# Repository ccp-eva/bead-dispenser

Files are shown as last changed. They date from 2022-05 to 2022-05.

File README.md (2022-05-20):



# CCP Bead Dispenser

**A DIY USB powered bead dispenser**

> Contains an Arduino sketch that accepts user input (i.e., an integer) and then starts a Nema 14 stepper motor. While the motor rotates, the attached infrared beam module counts objects which break the beam. The motor will stop when the object count equals the provided number by the user. This repo includes all 3d stl files and the construction manual.

---

- [CCP Bead Dispenser](#ccp-bead-dispenser)
  - [Demos](#demos)
  - [Overview](#overview)
    - [Power Supply](#power-supply)
    - [What’s happening](#whats-happening)
      - [Software](#software)
      - [Hardware](#hardware)
  - [Hardware Components](#hardware-components)
  - [Construction Manual](#construction-manual)
    - [Soldering Adafruit Shield on the Arduino](#soldering-adafruit-shield-on-the-arduino)
    - [Wiring the Stepper Motor on the Adafruit Shield](#wiring-the-stepper-motor-on-the-adafruit-shield)
      - [Check which coils make a pair](#check-which-coils-make-a-pair)
      - [Connect the Motor to the Shield](#connect-the-motor-to-the-shield)
    - [IR Breakbeam Sensors Connection](#ir-breakbeam-sensors-connection)
      - [Add DuPont Connectors to the wires](#add-dupont-connectors-to-the-wires)
    - [Connect IR Breakbeam Sensors](#connect-ir-breakbeam-sensors)
    - [Threading](#threading)
    - [Disk Treatment](#disk-treatment)
  - [3D Components Overview](#3d-components-overview)

---

## Demos

https://user-images.githubusercontent.com/9831678/168770235-a08dd8c6-3110-4d33-b17b-d08c474d0a74.mp4

https://user-images.githubusercontent.com/9831678/169273257-3fe446e2-8038-4976-b90e-d845b3b6b8b8.mp4

## Overview

This DIY bead dispenser was used as a companion apparatus for [Sarah Pope-Caldwell’s](https://sarahmichellepope.com/) _Nifty Shifty_ Game Battery. Specifically, the dispenser receives a signal (i.e., a positive integer) from the game, which starts a NEMA 14 stepper motor releasing the number of requested beads. The Arduino sketch was developed by [Steven Kalinke](https://www.eva.mpg.de/de/comparative-cultural-psychology/staff/steven-kalinke/).

Initially, [Dylan T Guenther](https://neurology.ufl.edu/profile/guenther-dylan/) provided us with his modifications from [thingiverse](https://www.thingiverse.com/thing:1771176) dispenser, and then [Raik Pieszek](https://www.eva.mpg.de/comparative-cultural-psychology/staff/raik-pieszek/) made significant modifications to meet our requirements. You will find all the `stl` files within the repository’s [`stl` directory](./stl/).

### Power Supply

We are aware the stepper motor and infrared beams are underpowered by the low voltage/current constraints of the USB 2 protocol (i.e., 5V @ 0.5A). However, throughout the entire hardware engineering process, we tested the dispenser to run with standard USB 2.0 power only and have not observed any drawbacks by under-powering it. The dispenser was also running in high humidity conditions (Congo) for approx. 8h per day over five to six weeks conducted by [Elisa Felsche](https://www.eva.mpg.de/comparative-cultural-psychology/staff/elisa-felsche/). Please refer to the [hardware components](#hardware-components) sections for further details.

### What’s happening

As of Summer 2022, we will work on a version 2 with some soft- and hardware improvements, which are listed below:

#### Software

Check the [issue tab](https://github.com/ccp-eva/bead-dispenser/issues) for open issues!

#### Hardware

- [ ] Use Gewindemuffen, -hülse, or Stangenmutter to replace the plastic pillows, Or better use Gewindestifte/Madenschrauben (M5/60mm) (https://www.fenau.eu/gewindeterminal-mit-innengewinde-linksgewinde-fuer-seil-von-o-3-mm-bis-o-8-mm-v2a.html)
- [ ] Make a design that allows flexible adjustment for the disk hole sizes
- [ ] Heat space for stepper motor
- [ ] Motor Thron
- [ ] Universal mount for the flexible funnel sizes

## Hardware Components

<!-- prettier-ignore -->
| Component                                                                   | Description                                                                                                                                                                                                                                                                                                 | Approx. Price |
| --------------------------------------------------------------------------- | :---------------------------------------------------------------------------------------------------------------------------------------------------------------------------------------------------------------------------------------------------------------------------------------------------------- | ------------- |
| Arduino Uno                                                                 | https://www.amazon.com/Arduino-A000066-ARDUINO-UNO-R3/dp/B008GRTSV6                                                                                                                                                                                                                                         |               |
| Adafruit Motor Shield (2.3)                                                 | https://www.amazon.com/Adafruit-Motor-Stepper-Shield-Arduino/dp/B00PUTH3B0                                                                                                                                                                                                                                  |               |
| … alternatively version 2.0 (cheaper)                                       | https://www.roboter-bausatz.de/p/motor-shield-v2.0-fuer-arduino?sPartner=8&gclid=CjwKCAjw1JeJBhB9EiwAV612y0uTo-yNJ4GlXUTTYTJsgV14ZZIoj7A12Il0sJB5pGVDDNJmeDUyexoCM9cQAvD_BwE                                                                                                                                |               |
| Stepper Motor (Nema 14) Option 1                                            | Polou SY35ST28-0504A (200 steps / 1.8°, 0.1Nm holding torque, 10V @ 0.5A, 20Ω Phase resistance) – [Datasheet](https://www.pololu.com/file/0J688/SY35ST28-0504A.pdf) – https://www.robotshop.com/de/de/10-v-05-a-13-oz-in-zweipoliger-schrittmotor.html                                                      |               |
| Stepper Motor (Nema 14) Option 2                                            | Joy-it Nema14-01 (200 steps / 1.8°, 0.1Nm holding torque, 8V @ 0.4A, 20Ω Phase resistance) — [Datasheet](https://joy-it.net/en/products/NEMA14-01) — https://joy-it.net/en/products/NEMA14-01 or https://www.conrad.de/de/p/joy-it-schrittmotor-nema14-01-0-1-nm-0-4-a-wellen-durchmesser-5-mm-2142507.html |               |
| Adafruit IR Beam Break Sensor Pair (3mm, preferably with DuPont Connectors) | https://www.mouser.de/ProductDetail/Adafruit/2167?qs=GURawfaeGuCJ0J7vogtCzg%3D%3D                                                                                                                                                                                                                           |               |
| USB Wire (Type B from the Arduino to whatever you need on your computer)    | Note, we had some difficulties with USB Adapters, a direct connection is preferred, e.g., USB C to Type B: [USB-Kabel USB 2.0 USB-B Stecker](https://www.conrad.de/de/p/manhattan-usb-kabel-usb-2-0-usb-b-stecker-usb-c-stecker-2-00-m-schwarz-2356814.html)                                                |               |
| Pellets                                                                     | We tested a variety of beads/pellets. A rule of thumb: beads should be a non-reflective surface, as the IR signal can be reflected around the pellet. Wood is good material; we used these wood balls: https://www.holz-allerlei.de/holzkugeln-ohne-bohrung/143/holzkugeln-6-mm-oe-ohne-bohrung?c=34        |               |
| Soldering Iron                                                              |                                                                                                                                                                                                                                                                                                             |               |
| Crimp tool and DuPont Connectors                                            | … to easily connect the IR beam break sensors                                                                                                                                                                                                                                                               |               |
| Threading tap to create threads                                             | … for screws and nuts (M4)                                                                                                                                                                                                                                                                                  |               |

## Construction Manual

### Soldering Adafruit Shield on the Arduino

- [Documentation](https://learn.adafruit.com/adafruit-motor-shield-v2-for-arduino/install-headers)
- [Guide](https://learn.adafruit.com/adafruit-motor-shield-v2-for-arduino/install-headers#installing-with-stacking-headers-405903-16)

- Place the Shield stacking headers on the Adafruit shield (terminals are optional for this setup) and solder them its bottom
- You may need to buy stacking headers as the Adafruit shield does not come with them (it did actually for our case)

<p align="middle">
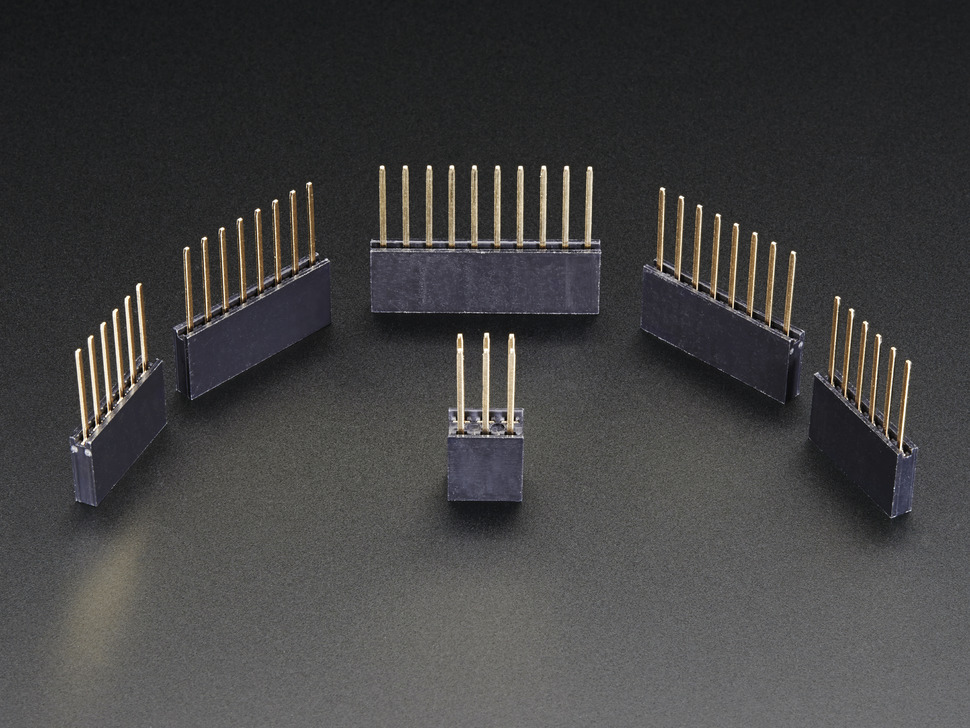
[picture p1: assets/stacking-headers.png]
  
  <br>
  Soldering stacking headers to the Motorshield (they may come pre-soldered for Motor Shield v.2.3)
</p>

### Wiring the Stepper Motor on the Adafruit Shield

#### Check which coils make a pair

Either use a Multimeter and figure out the two wires having the lowest resistance; those make a coil pair. If you do not have a Multimeter, connect their wire tips: Now turn the stepper motor: If the rotation resistance is high, the two cables belong together (i.e., making a coil pair).

#### Connect the Motor to the Shield

<p align="middle">
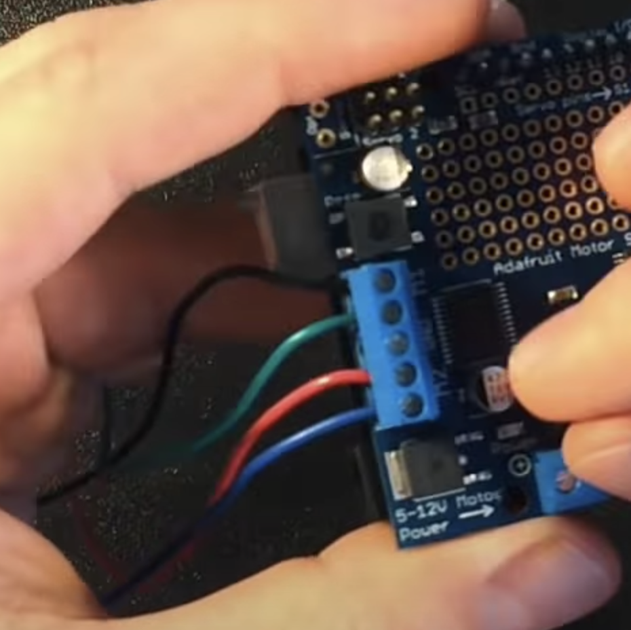
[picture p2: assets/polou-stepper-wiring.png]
  
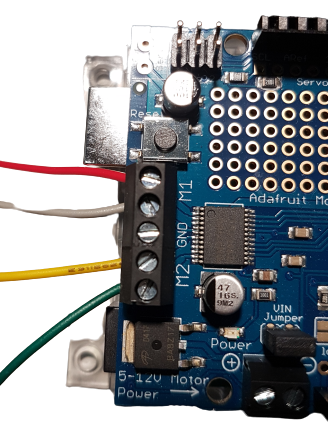
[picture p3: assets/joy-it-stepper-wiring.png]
  <br>
  Left: Polou SY35ST28-0504A (M1: black, green; M2: red, blue). Right: Joy-it Nema14 (M1: red, gray; M2: yellow, green).
</p>

### IR Breakbeam Sensors Connection

Docs & Datasheet: https://www.adafruit.com/product/2167

<p align="middle">
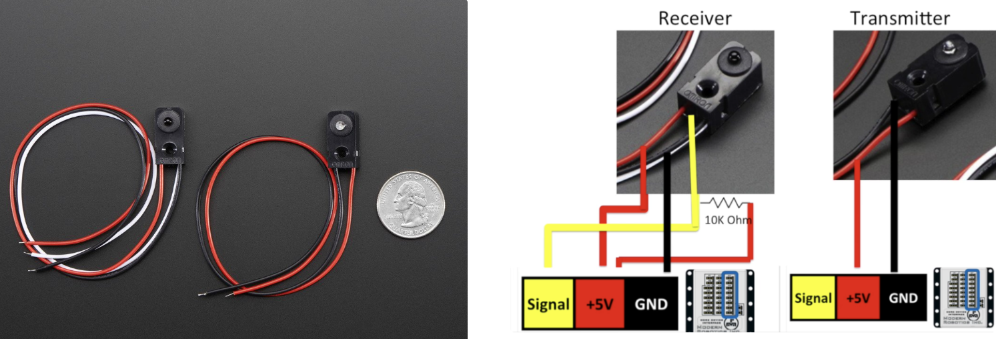
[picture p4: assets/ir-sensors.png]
  
  
  Left Image: The receiver is on the left; it has three wires. The transmitter is on the right; it has two wires.
</p>

#### Add DuPont Connectors to the wires

If your IR break beam sensors came with DuPont (see [JST connector - RE](https://en.wikipedia.org/wiki/JST_connector)) connectors, you can skip this step. If not, use a crimp tool to add crimps.

<p align="middle">
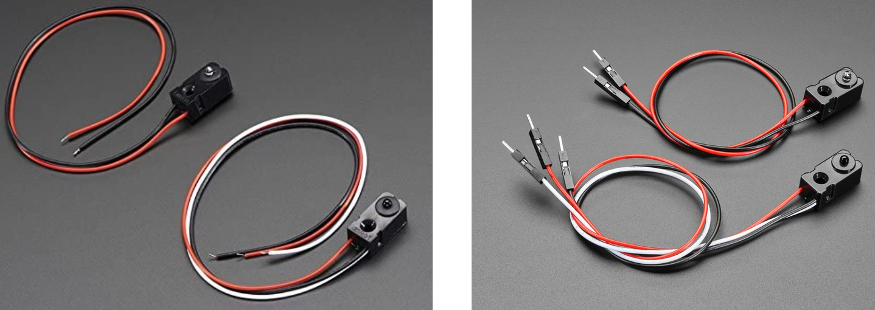
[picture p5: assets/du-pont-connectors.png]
  
  
  Left: IR Breakbeam Sensors w/o DuPont Connectors. Right: IR Breakbeam Sensors w/ DuPont Connectors.
</p>

### Connect IR Breakbeam Sensors

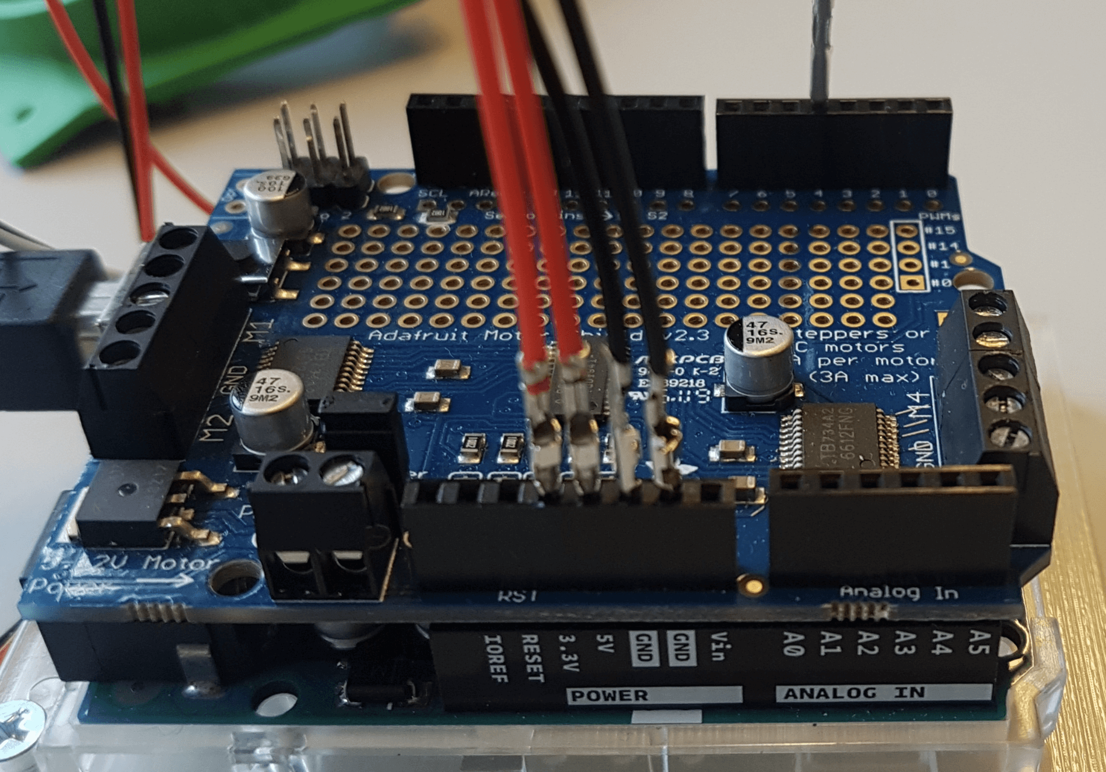
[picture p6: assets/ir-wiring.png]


The **receiver** (photodiode/sensor) has **three** colored wires; connect the

- **black** wire to the ground (there are two, which one doesn’t matter)
- **red** wire to the 5V Pin (**_important!_**)
- **white** wire to Pin 4 in the Digital I/O array

The **transmitter LED** (sender) has **two** colored wires; connect the

- **black** wire to the ground (the one that is left)
- **red** wire to the 3V Pin (**_important!_**)

### Threading

Use **M4 threading taps** for the following 3D components:

<!-- prettier-ignore -->
|  |  |
|-|-|
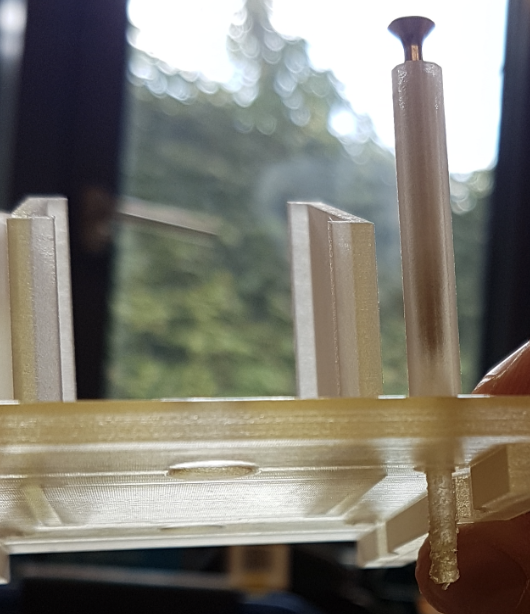
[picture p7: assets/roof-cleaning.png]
| The four pillars from the **roof** print-out (you may need to get rid of some residuals from the print before). Use a screw (or whatever) to push out residuals from the print. Thread after cleaning. |  |
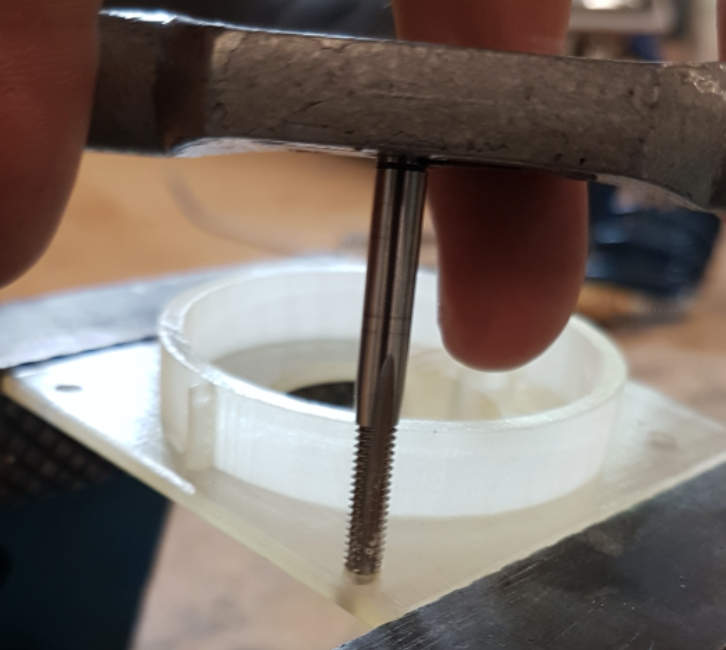
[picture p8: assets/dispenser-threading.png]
| The four holes from the **dispenser** holes |  |
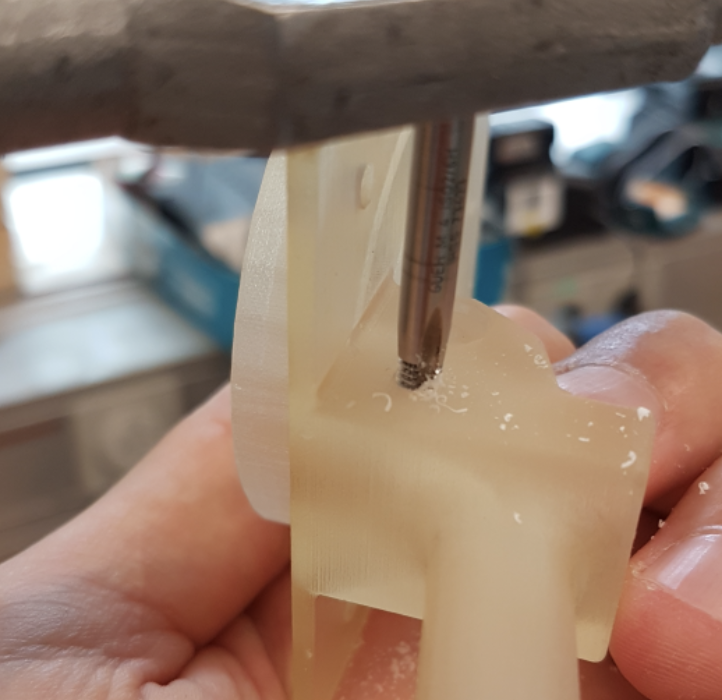
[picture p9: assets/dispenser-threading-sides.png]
| The side of the dispenser. Drill an M4 thread in the side of the dispenser as a fixation for the IR beam breaker |  |
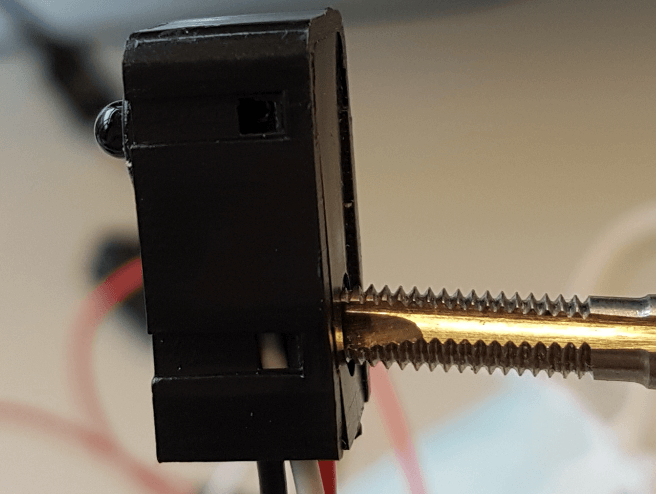
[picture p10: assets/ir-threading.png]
| Finally, drill an M4 thread in the IR break beam transmitter & receiver (this will be screwed together with the dispenser later.  |  |

### Disk Treatment

- Depending on the 3D printer, the bottom of the disk may be a bit rough, therefore creating resistance. Use fine sandpaper to reduce friction.
- Depending on the 3D printer, the disk’s hole may be too narrow for the stepper motor’s D-shaft. Roll a thin layer of sandpaper to increase the inner diameter.

<p align="middle">
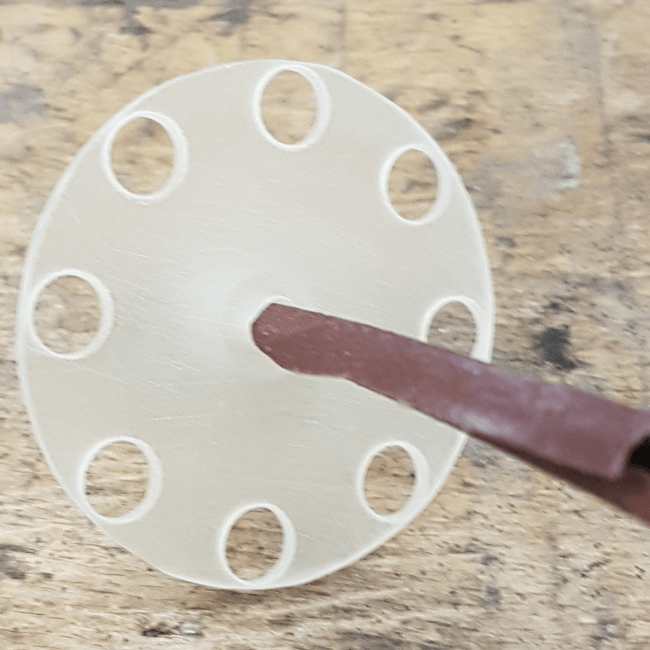
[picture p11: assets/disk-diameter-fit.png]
  
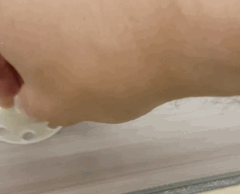
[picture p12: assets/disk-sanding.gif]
  <br>
  Left: Increase inner disk diameter. Right: Sandpaper the bottom of the disk.
</p>

## 3D Components Overview

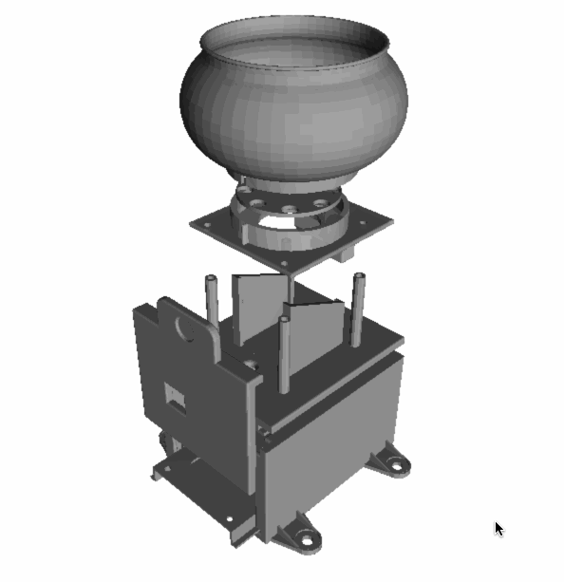
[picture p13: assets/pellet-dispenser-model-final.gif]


Our model is composed of seven components; these are from bottom to top:

- Box
- Slide
- Door
- Roof
- Dispenser
- Disk
- Funnel

<!-- prettier-ignore -->
| Component | STL File | Isometric Preview |
|-|-|-|
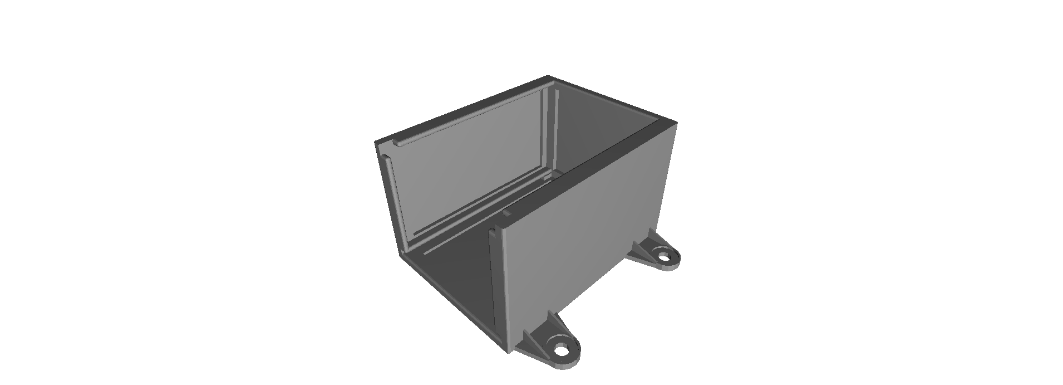
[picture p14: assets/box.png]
| **Box** — Housing for the Arduino & Adafruit Shield | [Download](stl/box.stl) |  |
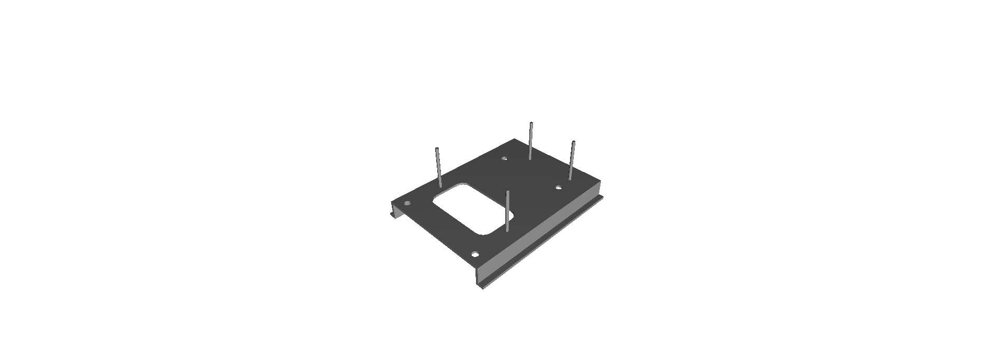
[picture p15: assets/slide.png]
| **Slide** — To fixate the Arduino’s plate with the slide | [Download](stl/slide.stl) |  |
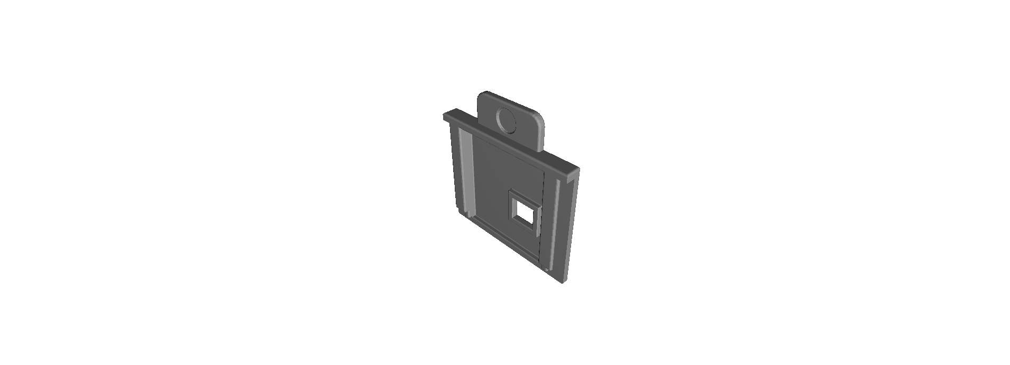
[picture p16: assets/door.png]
| **Door** — Sliding door that closes the box | [Download](stl/door.stl) |  |
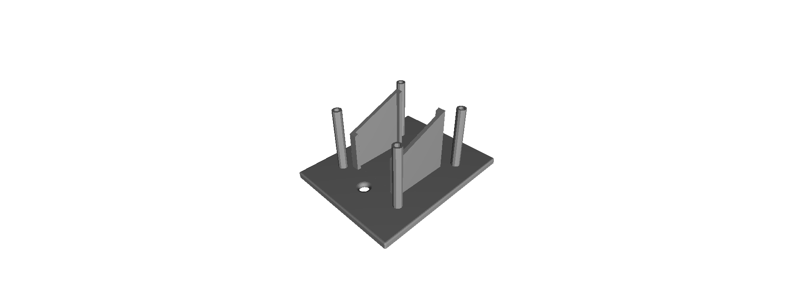
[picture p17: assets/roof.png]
| **Roof** — Coveres the box, and provides a housing for a NEMA 14 stepper motor | [Download](stl/roof.stl) |  |
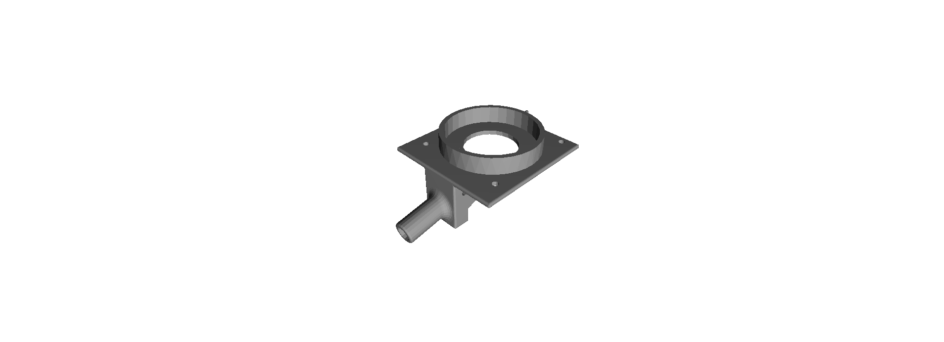
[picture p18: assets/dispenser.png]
| **Dispenser** — Holding the disc and provides a tube | [Download](stl/dispenser.stl) |  |
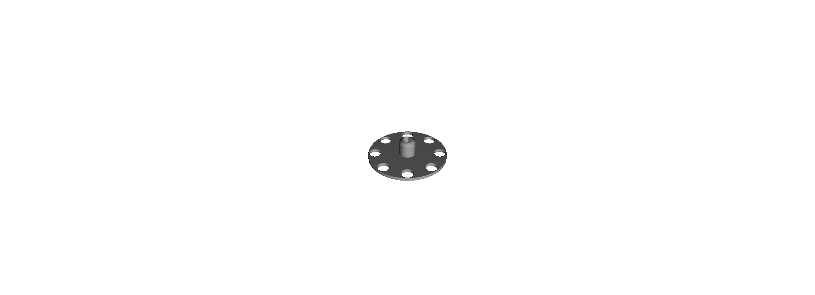
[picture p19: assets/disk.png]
| **Disk** — Revolving magazine to release beads or other objects | [Download](stl/disk.stl) |  |
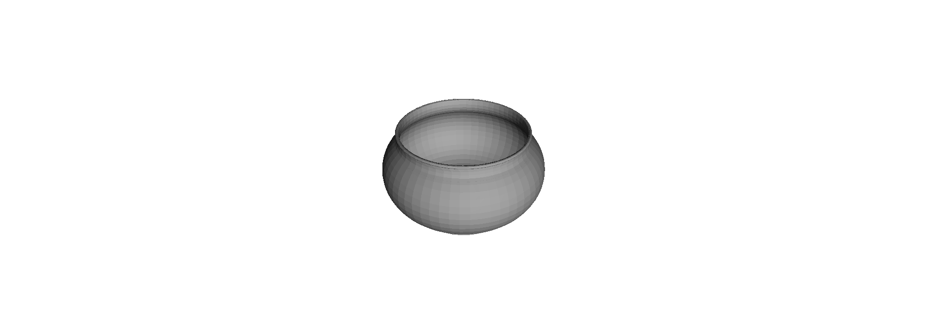
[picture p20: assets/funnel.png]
| **Funnel** — Bead funnel/storage unit | [Download](stl/funnel.stl) |  |
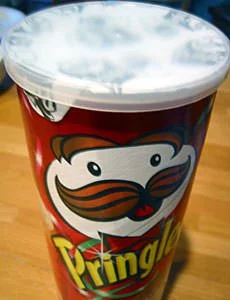
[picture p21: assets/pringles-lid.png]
| **Lid** — Get yourself some Pringles. Use the Pringle’s lid to seal the funnel. (optional) | — |  |

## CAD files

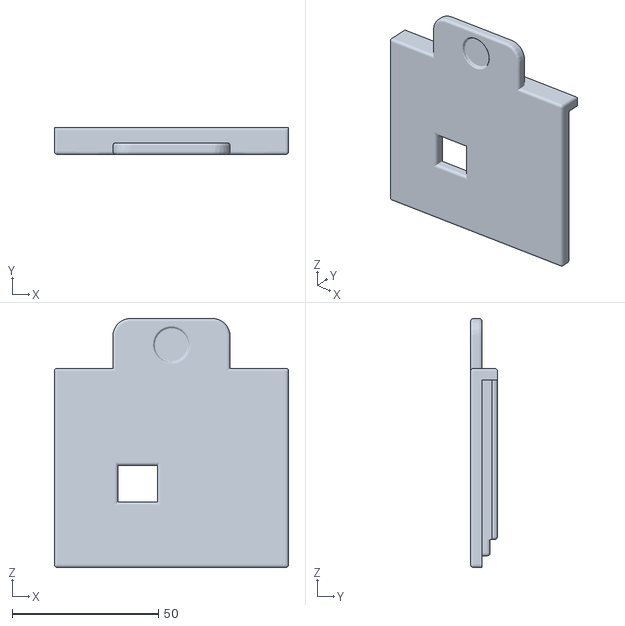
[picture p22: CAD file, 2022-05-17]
stl/door.stl
80.0 x 9.20 x 85.0

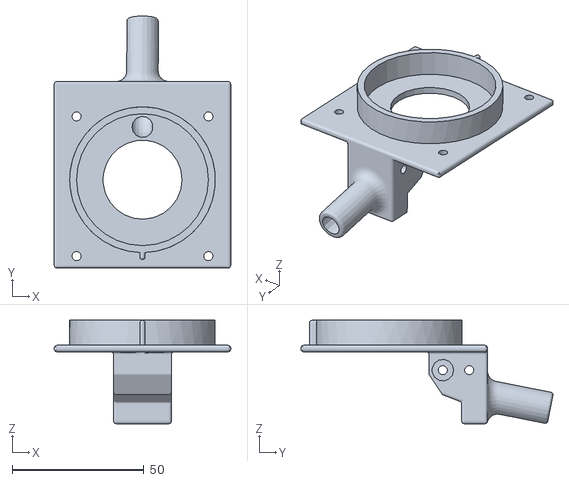
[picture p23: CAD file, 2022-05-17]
stl/dispenser.stl
67.0 x 95.6 x 39.3

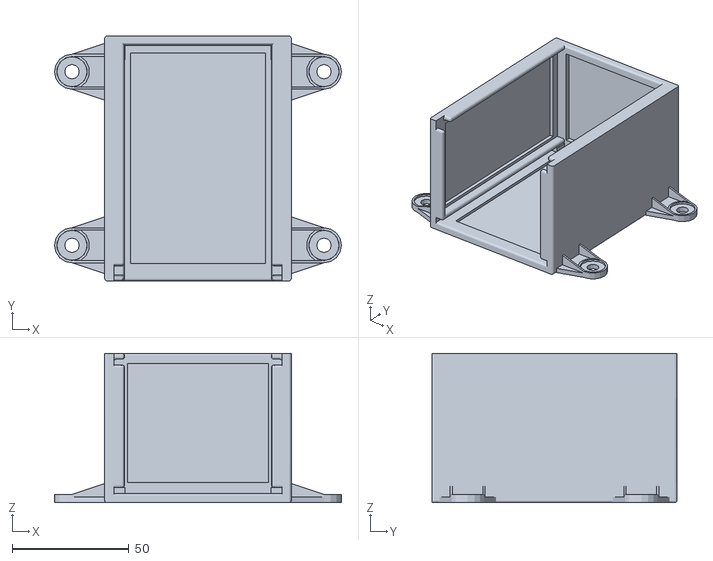
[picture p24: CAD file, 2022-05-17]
stl/box.stl
123.0 x 105.0 x 64.0

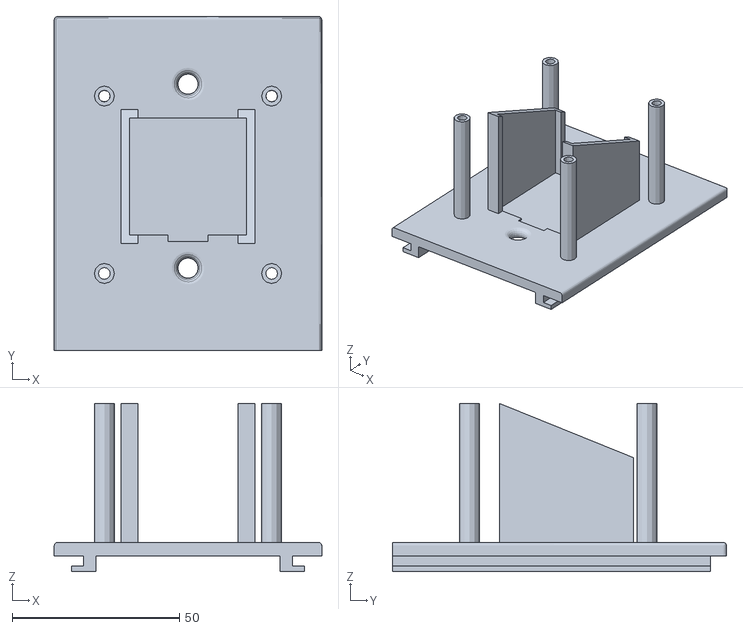
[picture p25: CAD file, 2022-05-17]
stl/roof.stl
80.0 x 99.8 x 50.2

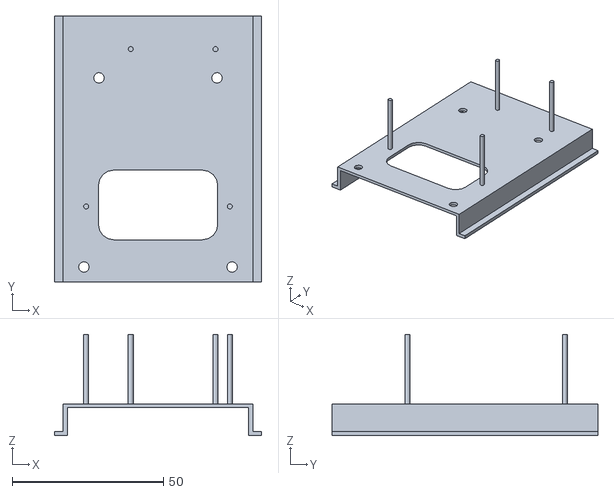
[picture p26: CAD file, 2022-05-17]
stl/slide.stl
68.6 x 87.9 x 33.4

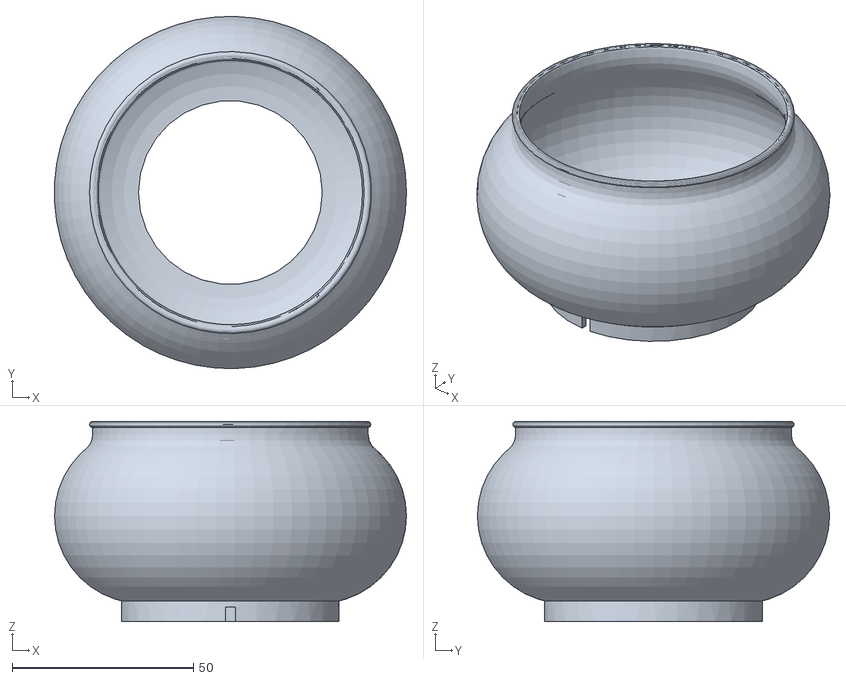
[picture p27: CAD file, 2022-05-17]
stl/funnel.stl
97.0 x 97.0 x 55.2

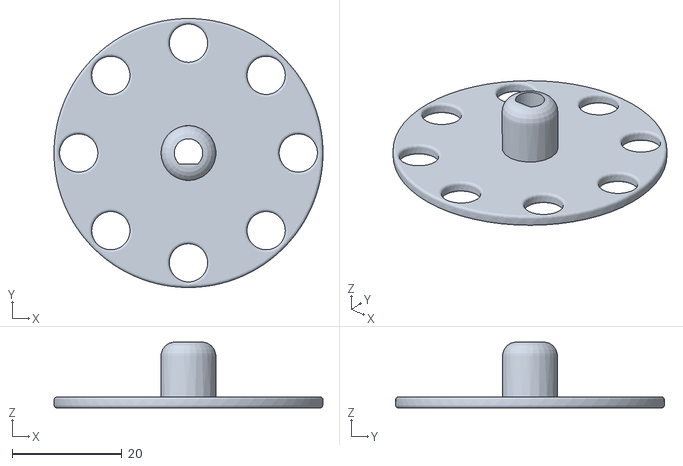
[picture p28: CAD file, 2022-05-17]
stl/disk.stl
49.0 x 49.0 x 12.0

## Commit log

2021-01-28 Remove LED Code parts, since we don’t use LEDs
2021-02-01 Use more verbose sensor code
2021-02-02 Remove LED Parts for now
2021-02-02 Include Stepper Motor Functionality
2021-06-30 Add AccelStepper library to make motor independent
2022-05-17 add stl files
    [box.stl, disk.stl, dispenser.stl, door.stl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]
